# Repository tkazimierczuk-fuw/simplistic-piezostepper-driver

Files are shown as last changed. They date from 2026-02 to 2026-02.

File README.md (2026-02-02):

# A Simplistic Driver for Slip-Stick Piezo Positioners

This project presents a minimalistic, low-cost driver for slip-stick piezo positioners.

Conventional slip-stick piezo drivers typically rely on operational amplifiers to generate sawtooth waveforms. While this approach gives the most control over the stage, driving highly capacitive piezo loads with op-amps requires careful compensation and layout to avoid instability and self-oscillations.

In contrast, this driver avoids operational amplifiers altogether. Instead, the piezo load is driven directly using simple MOSFET stages. This significantly simplifies the circuit and improves robustness when dealing with capacitive loads, making the design well suited for ad-hoc, experimental, or budget-constrained setups.

The goal of this project is not ultimate performance, but practicality: providing a straightforward and reliable way to generate slip-stick drive signals with minimal component count and design overhead.

## Usage

The driver is straightforward - just connect your slip-stick piezo stage and use 3-way lever-switch to jog the stage. The step amplitude is fixed at 28 V and the step frequency is fixed (in the firmware) at 300 Hz. This values are suitable, e.g. for Attocube ANP series.

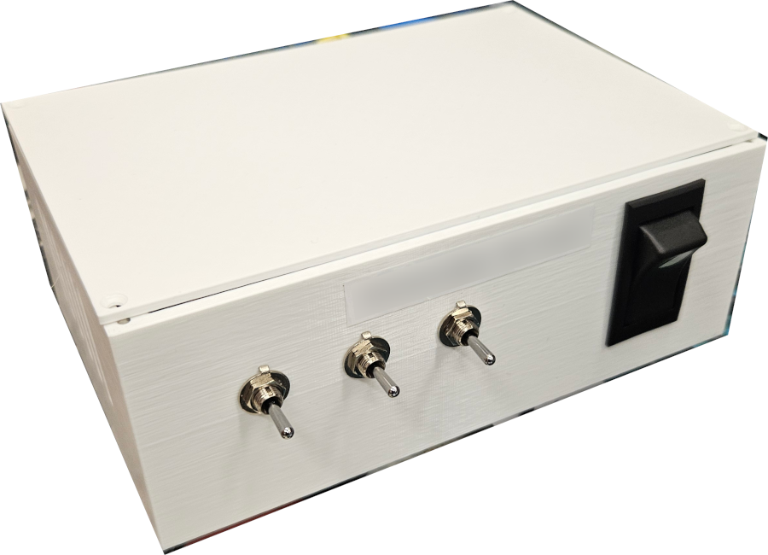
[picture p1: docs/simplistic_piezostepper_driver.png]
The driver enclosed in a 3D case


The circuit contains a PPTC resettable fuse which trips when we try to drive the short-circuit. It automatically resets upon switching the device off. 

## How it works

The driver generates the characteristic slip-stick waveform by charging and discharging the piezo capacitance directly through MOSFET switches, rather than through linear amplifiers. One stage provides a relatively slow voltage ramp (stick phase), while the other rapidly discharges the piezo (slip phase). Rapid charge/discharge is realized by linking the piezo to VCC/GND directly by a MOSFET. Slow ramp is realized by introducing an extra resistor R in series with the MOSFET. The time-constant of the slope is governed by a product of resistance R and the capacitance of the piezo stage.

Each of 3 modules has the same design:

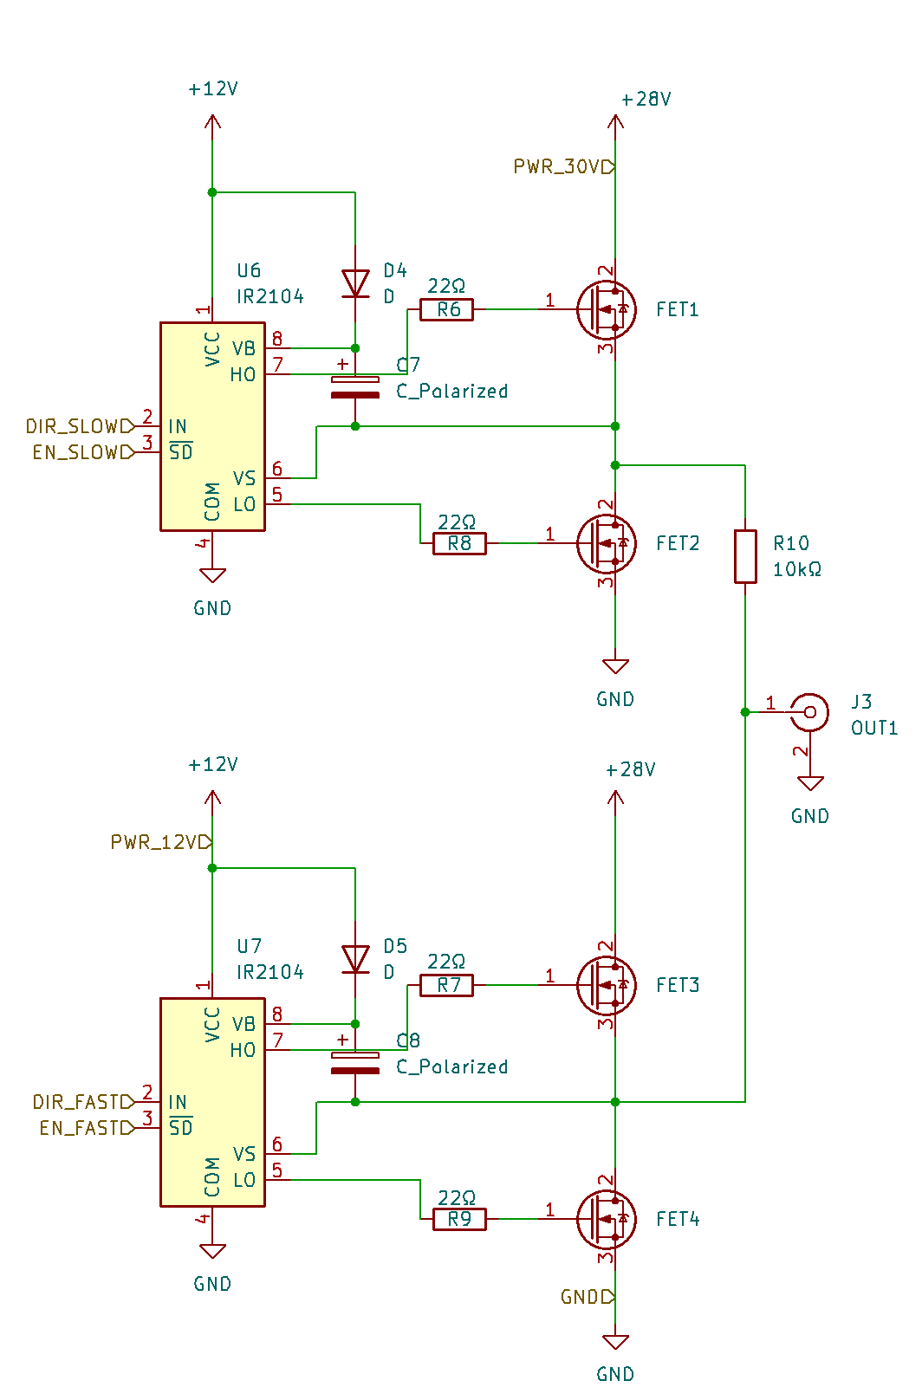
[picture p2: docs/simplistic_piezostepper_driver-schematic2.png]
Simplistic piezo stepper driver schematic


## What to buy (typical components)

Exact values and footprints are given in the schematics/PCB files, but the design generally requires only common parts:

- 12x N-channel MOSFETs, e.g. STP55NF06L
- 6x half-bridge driver, e.g. IR2104STRPBF
- 3x BNC connector, e.g. R-128
- 3x lever switch, e.g. 1-1825139-8
- 1x power switch, e.g. R13-220BA-01-BBG (oversized)
- Raspberry Pico
- SMD 1206 elements: 7x diode, resistors: 1x 1MΩ, 6x 100kΩ, 12x 22Ω, 3x 10kΩ
- THT capacitors
- a polymer fuse, e.g. 0ZCJ0020FF2E
- DC supply socket, e.g. PJ-063AH
- step-up converter, e.g. MT3608 

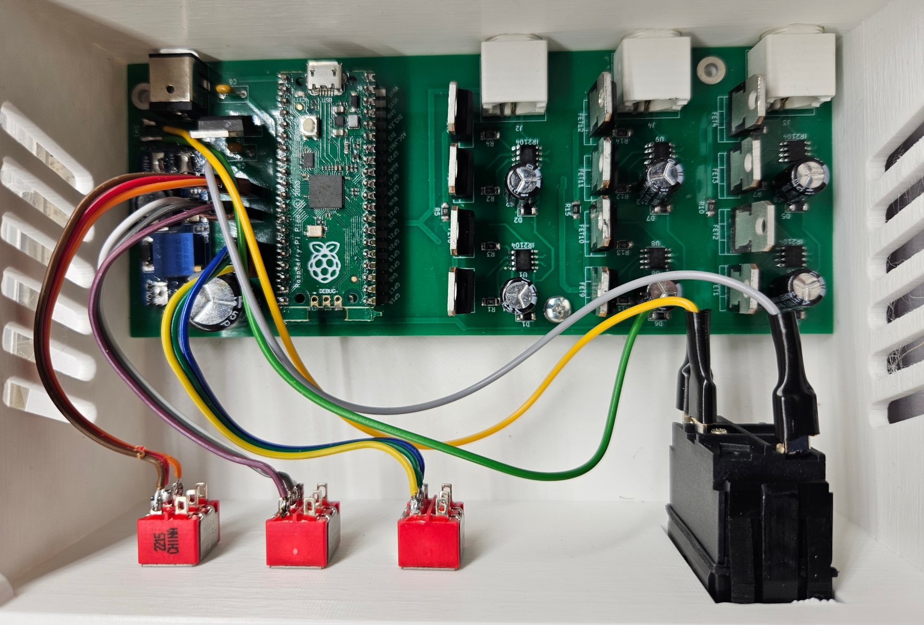
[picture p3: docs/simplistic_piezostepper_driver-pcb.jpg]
Fully populated PCB


## License & Disclaimer

This project is released under the MIT License. You are free to use, modify, and distribute it according to the terms of that license.

The design is provided as-is, without any warranties or guarantees of performance, safety, or suitability for any particular purpose. This is a research/DIY project; use it at your own risk.

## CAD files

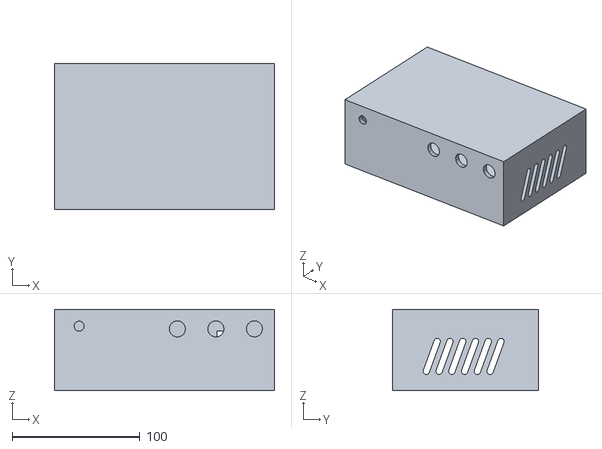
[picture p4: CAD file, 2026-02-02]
case/case_for_3dprint.stl
172.4 x 114.4 x 63.5

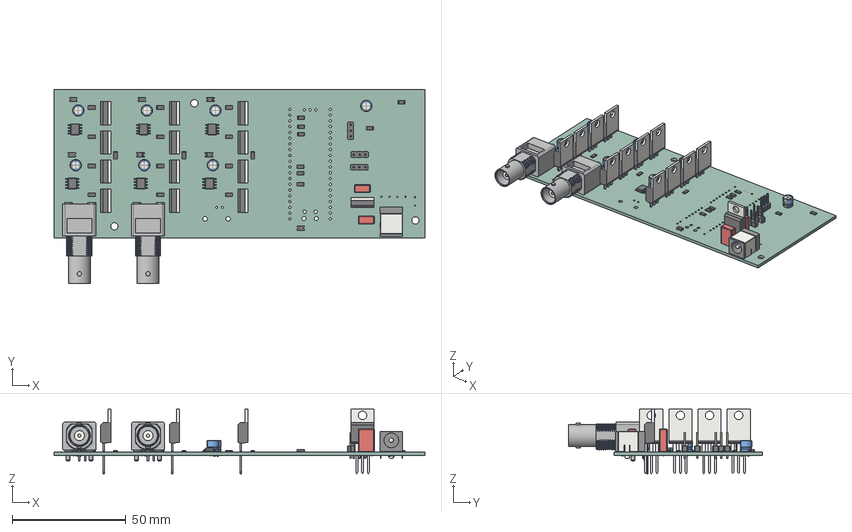
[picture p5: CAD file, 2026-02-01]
pcb/simplistic-piezostepper-driver.step
163.4 x 85.3 x 28.5 mm
C_Rect_L7.0mm_W3.5mm_P5.00mm x 2
D_1206_3216Metric x 7
SOIC-8_3.9x4.9mm_P1.27mm x 6
R_1206_3216Metric x 23
TO-220-3_Vertical x 13
BarrelJack_CUI_PJ-063AH_Horizontal
CP_Radial_D5.0mm_P2.00mm x 7
BNC_Amphenol_B6252HB-NPP3G-50_Horizontal x 2
Pico
PinHeader_1x03_P2.54mm_Vertical x 3
homemade_attocube_PCB

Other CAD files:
case/case_for_3dprint.ipt

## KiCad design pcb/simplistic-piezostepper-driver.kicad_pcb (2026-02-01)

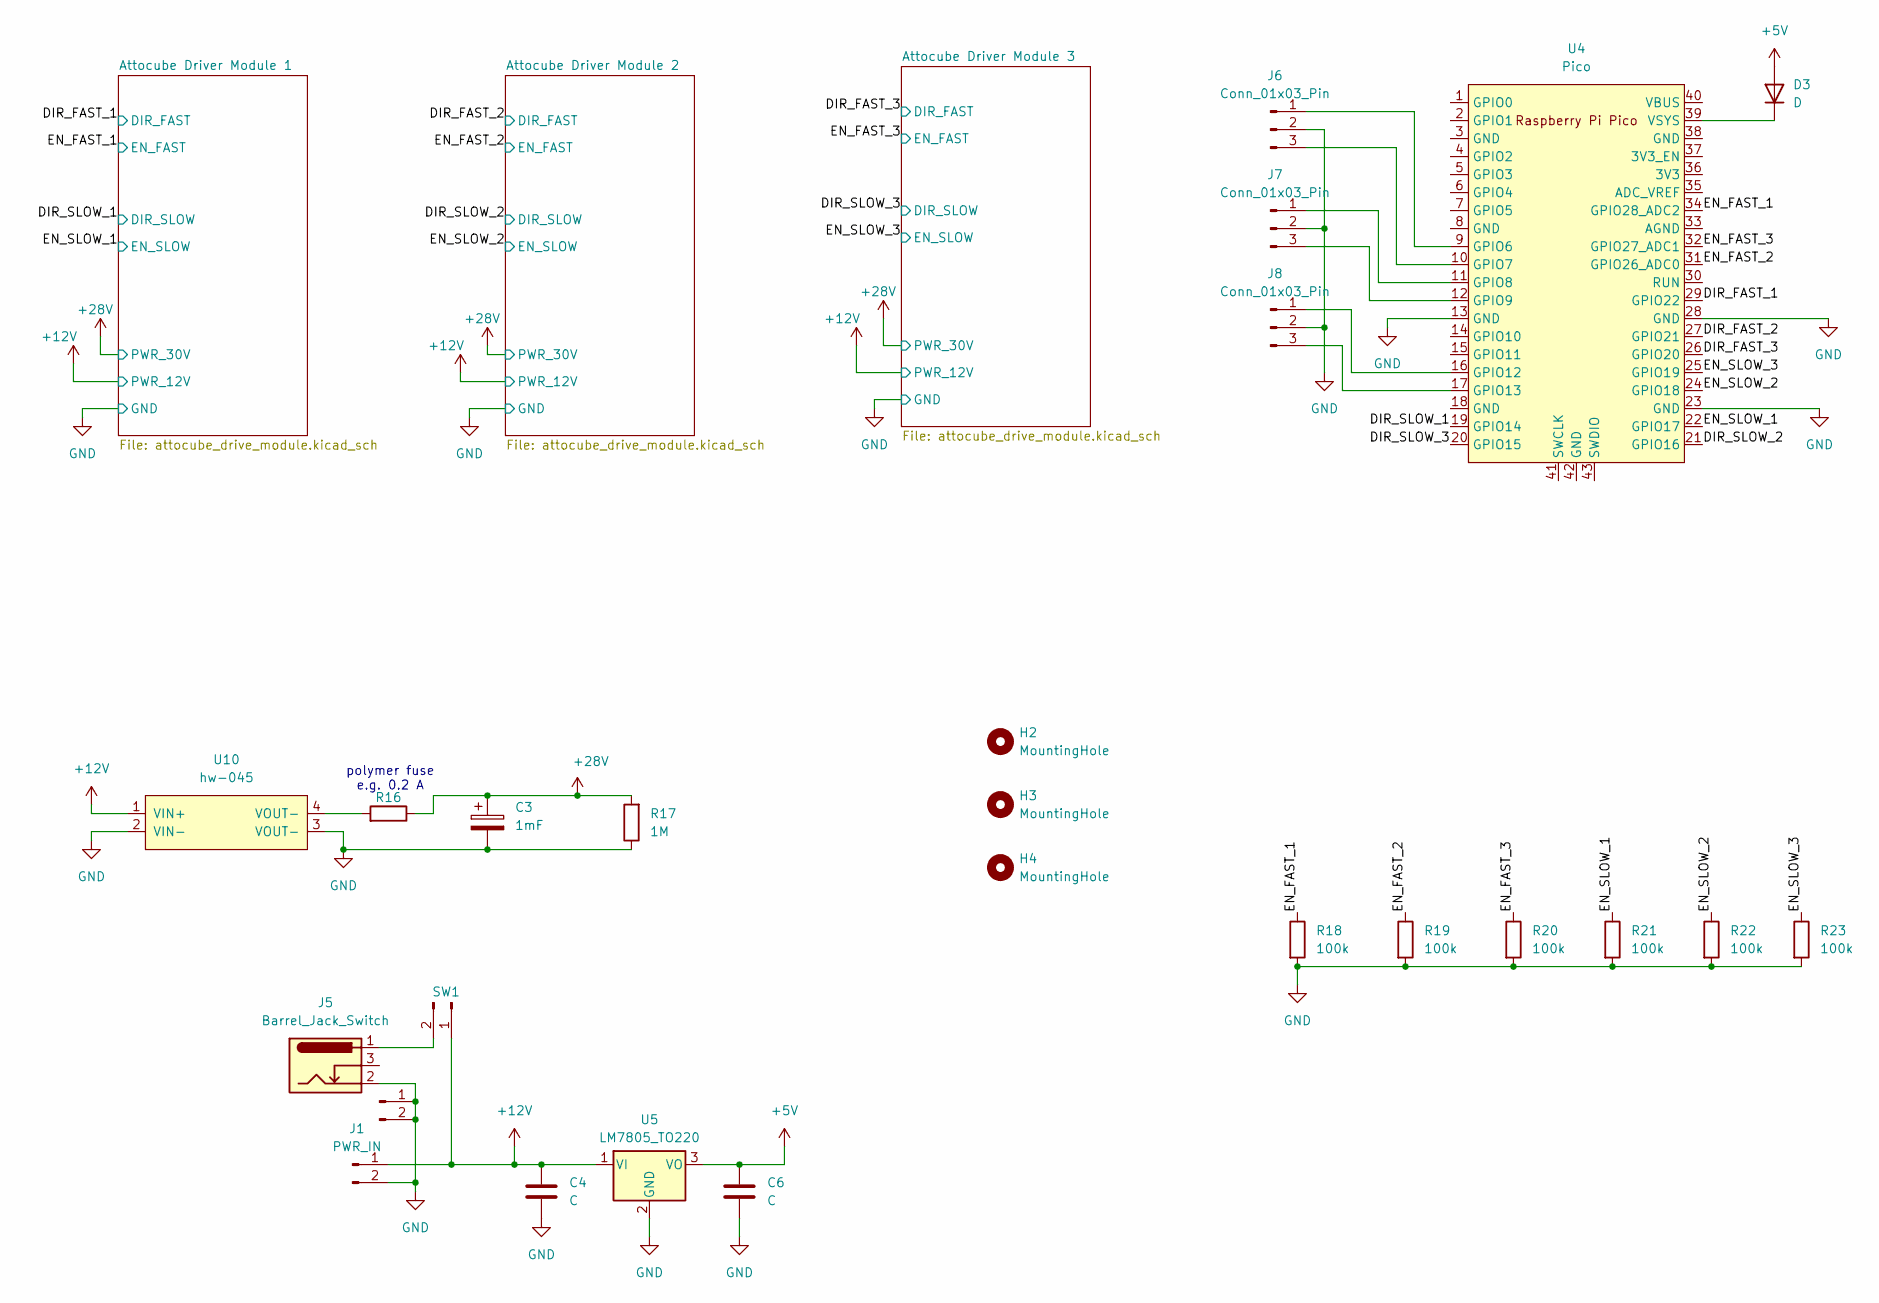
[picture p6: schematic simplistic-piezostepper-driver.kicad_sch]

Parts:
C3: 1mF; CP_Radial_D5.0mm_P2.00mm
C4, C6: C; C_Rect_L7.0mm_W3.5mm_P5.00mm
D3: D; D_1206_3216Metric_Pad1.42x1.75mm_HandSolder
H2, H3, H4: MountingHole; MountingHole_3.2mm_M3_Pad
J1: PWR_IN; SolderWire-0.1sqmm_1x02_P3.6mm_D0.4mm_OD1mm
J5: Barrel_Jack_Switch; BarrelJack_CUI_PJ-063AH_Horizontal
J6, J7, J8: Conn_01x03_Pin; PinHeader_1x03_P2.54mm_Vertical
J10: Conn_01x02_Pin; SolderWire-0.1sqmm_1x02_P3.6mm_D0.4mm_OD1mm
R16: 10?; R_1206_3216Metric_Pad1.30x1.75mm_HandSolder
R17: 1M; R_1206_3216Metric_Pad1.30x1.75mm_HandSolder
R18, R19, R20, R21, R22, R23: 100k; R_1206_3216Metric_Pad1.30x1.75mm_HandSolder
SW1: Conn_01x02_Pin; SolderWire-0.1sqmm_1x02_P3.6mm_D0.4mm_OD1mm
U4: Pico; RPi_Pico_SMD_TH
U5: LM7805_TO220; TO-220-3_Vertical
U10: hw-045

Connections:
+5V: C6.1, D3.2 (A), U5.3 (VO)
+12V: C4.1, J1.1, SW1.1, U5.1 (VI), U10.1 (VIN+); also elsewhere on the board
+28V: C3.1, R16.1, R17.2; also elsewhere on the board
/DIR_FAST_1: U4.29 (GPIO22); also elsewhere on the board
/DIR_FAST_2: U4.27 (GPIO21); also elsewhere on the board
/DIR_FAST_3: U4.26 (GPIO20); also elsewhere on the board
/DIR_SLOW_1: U4.19 (GPIO14); also elsewhere on the board
/DIR_SLOW_2: U4.21 (GPIO16); also elsewhere on the board
/DIR_SLOW_3: U4.20 (GPIO15); also elsewhere on the board
/EN_FAST_1: R18.1, U4.34 (GPIO28_ADC2); also elsewhere on the board
/EN_FAST_2: R19.1, U4.31 (GPIO26_ADC0); also elsewhere on the board
/EN_FAST_3: R20.1, U4.32 (GPIO27_ADC1); also elsewhere on the board
/EN_SLOW_1: R21.1, U4.22 (GPIO17); also elsewhere on the board
/EN_SLOW_2: R22.1, U4.24 (GPIO18); also elsewhere on the board
/EN_SLOW_3: R23.1, U4.25 (GPIO19); also elsewhere on the board
GND: C3.2, C4.2, C6.2, J1.2, J5.2, J6.2, J7.2, J8.2, J10.1, J10.2, R17.1, R18.2, R19.2, R20.2, R21.2, R22.2, R23.2, U4.13 (GND), U4.23 (GND), U4.28 (GND), U5.2 (GND), U10.2 (VIN-), U10.3 (VOUT-); also elsewhere on the board
unnamed: D3.1 (K), U4.39 (VSYS)
unnamed: J6.1, U4.9 (GPIO6)
unnamed: J6.3, U4.10 (GPIO7)
unnamed: J7.1, U4.11 (GPIO8)
unnamed: J7.3, U4.12 (GPIO9)
unnamed: J8.1, U4.16 (GPIO12)
unnamed: J8.3, U4.17 (GPIO13)
unnamed: R16.2, U10.4 (VOUT-)
unnamed: J5.1, SW1.2

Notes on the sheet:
polymer fuse e.g. 0.2 A

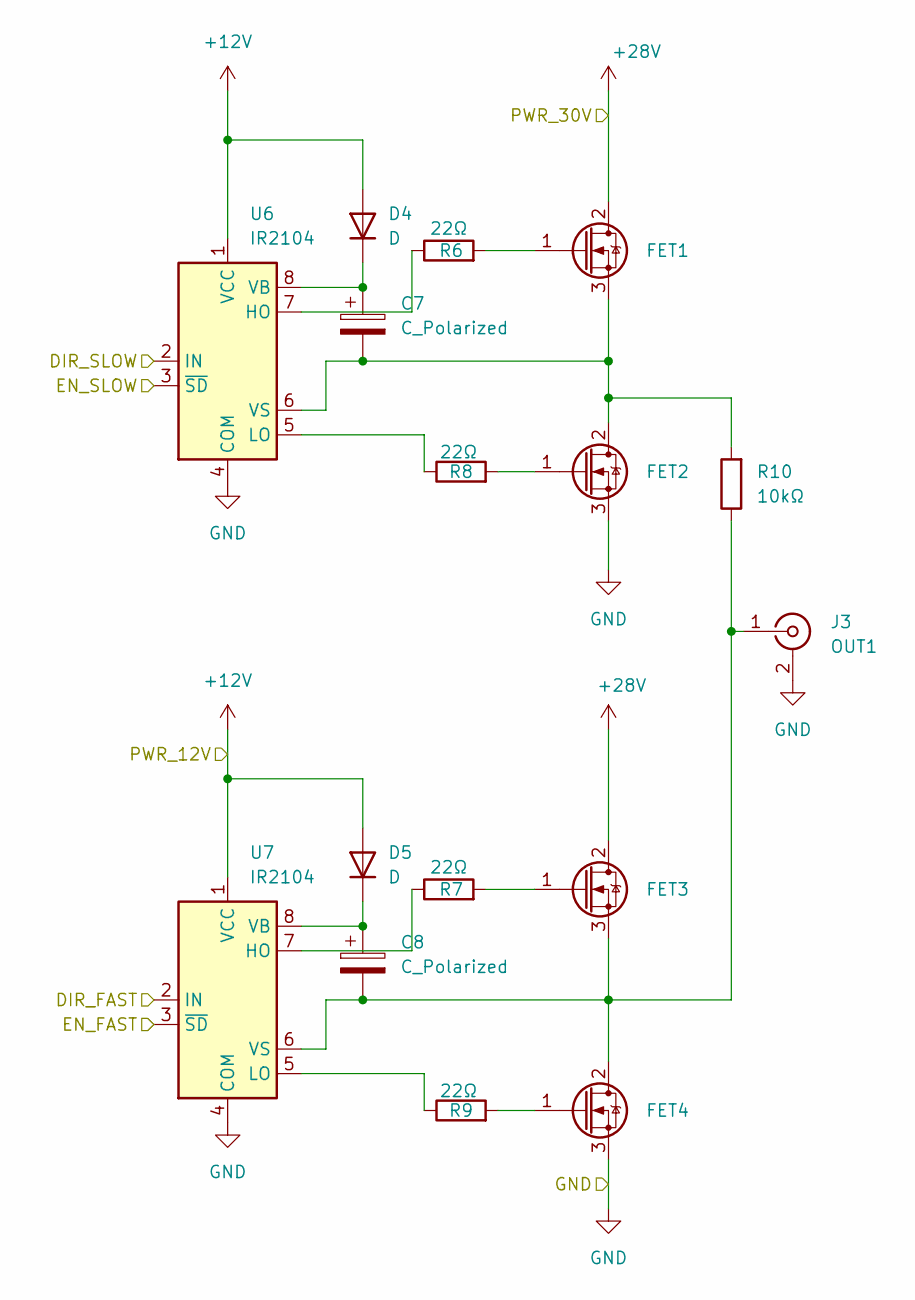
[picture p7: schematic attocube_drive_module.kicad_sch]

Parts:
C7, C8: C_Polarized; CP_Radial_D5.0mm_P2.00mm
D4, D5: D; D_1206_3216Metric_Pad1.42x1.75mm_HandSolder
FET1, FET2, FET3, FET4: Q_NMOS_Depletion_GDS; TO-220-3_Vertical
J3: OUT1; BNC_Amphenol_B6252HB-NPP3G-50_Horizontal
R6, R7, R8, R9: 22Ω; R_1206_3216Metric_Pad1.30x1.75mm_HandSolder
R10: 10kΩ; R_1206_3216Metric_Pad1.30x1.75mm_HandSolder
U6, U7: IR2104; SOIC-8_3.9x4.9mm_P1.27mm

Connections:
+12V: D4.2 (A), D5.2 (A), U6.1 (VCC), U7.1 (VCC); also elsewhere on the board
+28V: FET1.2 (D), FET3.2 (D); also elsewhere on the board
/DIR_FAST_1: U7.2 (IN); also elsewhere on the board
/DIR_SLOW_1: U6.2 (IN); also elsewhere on the board
/EN_FAST_1: U7.3 (~SD); also elsewhere on the board
/EN_SLOW_1: U6.3 (~SD); also elsewhere on the board
GND: FET2.3 (S), FET4.3 (S), J3.2 (Ext), U6.4 (COM), U7.4 (COM); also elsewhere on the board
unnamed: C7.1, D4.1 (K), U6.8 (VB)
unnamed: C8.1, D5.1 (K), U7.8 (VB)
unnamed: FET1.1 (G), R6.2
unnamed: C7.2, FET1.3 (S), FET2.2 (D), R10.2, U6.6 (VS)
unnamed: FET2.1 (G), R8.2
unnamed: FET3.1 (G), R7.2
unnamed: C8.2, FET3.3 (S), FET4.2 (D), J3.1 (In), R10.1, U7.6 (VS)
unnamed: FET4.1 (G), R9.2
unnamed: R6.1, U6.7 (HO)
unnamed: R8.1, U6.5 (LO)
unnamed: R7.1, U7.7 (HO)
unnamed: R9.1, U7.5 (LO)

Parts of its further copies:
C1, C2, C11, C12: C_Polarized; CP_Radial_D5.0mm_P2.00mm
D1, D2, D6, D7: D; D_1206_3216Metric_Pad1.42x1.75mm_HandSolder
FET5, FET6, FET7, FET8, FET9, FET10, FET11, FET12: Q_NMOS_Depletion_GDS; TO-220-3_Vertical
J2, J4: OUT1; BNC_Amphenol_B6252HB-NPP3G-50_Horizontal
R1, R2, R3, R4, R11, R12, R13, R14: 22Ω; R_1206_3216Metric_Pad1.30x1.75mm_HandSolder
R5, R15: 10kΩ; R_1206_3216Metric_Pad1.30x1.75mm_HandSolder
U1, U2, U8, U9: IR2104; SOIC-8_3.9x4.9mm_P1.27mm

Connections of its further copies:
+12V: D1.2 (A), D2.2 (A), D6.2 (A), D7.2 (A), U1.1 (VCC), U2.1 (VCC), U8.1 (VCC), U9.1 (VCC); also elsewhere on the board
+28V: FET5.2 (D), FET7.2 (D), FET9.2 (D), FET11.2 (D); also elsewhere on the board
/DIR_FAST_2: U2.2 (IN); also elsewhere on the board
/DIR_FAST_3: U9.2 (IN); also elsewhere on the board
/DIR_SLOW_2: U1.2 (IN); also elsewhere on the board
/DIR_SLOW_3: U8.2 (IN); also elsewhere on the board
/EN_FAST_2: U2.3 (~SD); also elsewhere on the board
/EN_FAST_3: U9.3 (~SD); also elsewhere on the board
/EN_SLOW_2: U1.3 (~SD); also elsewhere on the board
/EN_SLOW_3: U8.3 (~SD); also elsewhere on the board
GND: FET6.3 (S), FET8.3 (S), FET10.3 (S), FET12.3 (S), J2.2 (Ext), J4.2 (Ext), U1.4 (COM), U2.4 (COM), U8.4 (COM), U9.4 (COM); also elsewhere on the board
unnamed: C1.1, D1.1 (K), U1.8 (VB)
unnamed: C2.1, D2.1 (K), U2.8 (VB)
unnamed: C11.1, D6.1 (K), U8.8 (VB)
unnamed: C12.1, D7.1 (K), U9.8 (VB)
unnamed: FET5.1 (G), R1.2
unnamed: C1.2, FET5.3 (S), FET6.2 (D), R5.2, U1.6 (VS)
unnamed: FET6.1 (G), R3.2
unnamed: FET7.1 (G), R2.2
unnamed: C2.2, FET7.3 (S), FET8.2 (D), J2.1 (In), R5.1, U2.6 (VS)
unnamed: FET8.1 (G), R4.2
unnamed: FET9.1 (G), R11.2
unnamed: C11.2, FET9.3 (S), FET10.2 (D), R15.2, U8.6 (VS)
unnamed: FET10.1 (G), R13.2
unnamed: FET11.1 (G), R12.2
unnamed: C12.2, FET11.3 (S), FET12.2 (D), J4.1 (In), R15.1, U9.6 (VS)
unnamed: FET12.1 (G), R14.2
unnamed: R1.1, U1.7 (HO)
unnamed: R3.1, U1.5 (LO)
unnamed: R2.1, U2.7 (HO)
unnamed: R4.1, U2.5 (LO)
unnamed: R11.1, U8.7 (HO)
unnamed: R13.1, U8.5 (LO)
unnamed: R12.1, U9.7 (HO)
unnamed: R14.1, U9.5 (LO)

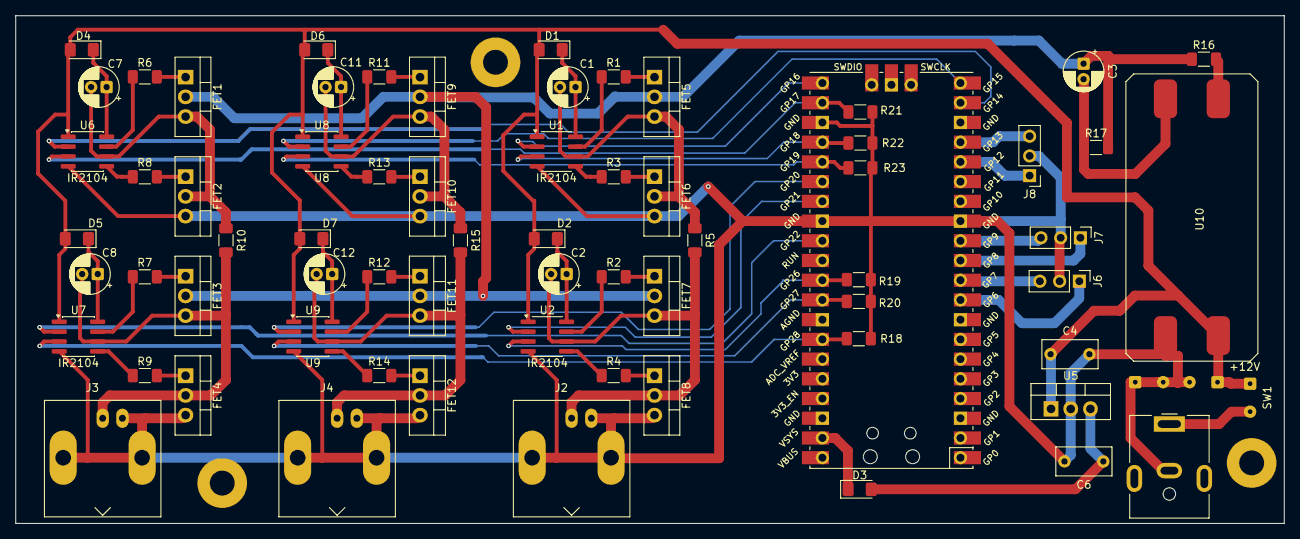
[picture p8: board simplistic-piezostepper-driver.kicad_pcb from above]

Board: 2 copper layers, 163.4 x 65.4 mm, 73 parts (0 on the bottom side), 61 nets.

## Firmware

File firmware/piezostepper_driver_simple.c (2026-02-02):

#include <stdio.h>
#include "pico/stdlib.h"

const int STEP_FREQ = 500;

// Channel pin definitions
typedef struct {
    int up_control_pin;
    int down_control_pin;
    int dir_fast_pin;
    int dir_slow_pin;
    int en_fast_pin;
    int en_slow_pin;
} ChannelPins;

// Channel 1 pins
const ChannelPins channel1_pins = {
    .up_control_pin = 6,
    .down_control_pin = 7,
    .dir_fast_pin = 22,
    .dir_slow_pin = 14,
    .en_fast_pin = 28,
    .en_slow_pin = 17
};

// Channel 2 pins
const ChannelPins channel2_pins = {
    .up_control_pin = 8,
    .down_control_pin = 9,
    .dir_fast_pin = 21,
    .dir_slow_pin = 16,
    .en_fast_pin = 26,
    .en_slow_pin = 18
};

// Channel 3 pins
const ChannelPins channel3_pins = {
    .up_control_pin = 12,
    .down_control_pin = 13,
    .dir_fast_pin = 20,
    .dir_slow_pin = 15,
    .en_fast_pin = 27,
    .en_slow_pin = 19
};

const ChannelPins* all_channels[] = {&channel1_pins, &channel2_pins, &channel3_pins};
const int num_channels = sizeof(all_channels) / sizeof(all_channels[0]);


typedef enum {
    IDLE,
    SLOW_UP,
    SLOW_DOWN,
    FAST_UP,
    FAST_DOWN
} ChannelState;

ChannelState state[] = {IDLE, IDLE, IDLE};



void initialize_gpio() {
    for (int i = 0; i < num_channels; i++) {
        const ChannelPins* channel = all_channels[i];

        // Configure control pins as inputs with pull-ups
        gpio_init(channel->up_control_pin);
        gpio_set_dir(channel->up_control_pin, GPIO_IN);
        gpio_pull_up(channel->up_control_pin);

        gpio_init(channel->down_control_pin);
        gpio_set_dir(channel->down_control_pin, GPIO_IN);
        gpio_pull_up(channel->down_control_pin);

        // Configure dir and en pins as outputs, initially low
        const int output_pins[] = {
            channel->dir_fast_pin, channel->dir_slow_pin,
            channel->en_fast_pin, channel->en_slow_pin
        };
        for (int j = 0; j < sizeof(output_pins) / sizeof(output_pins[0]); j++) {
            uint pin = output_pins[j];
            gpio_set_dir(pin, GPIO_OUT);
            gpio_init(pin);
            gpio_set_dir(pin, GPIO_OUT);
            gpio_put(pin, 0);
            state[i] = IDLE;
        }
    }
}

const int SLOW_STATE_RATIO = 4 ; // relative duration of the slow rise/fall phase
const int DELAY_US = 1000000L / (STEP_FREQ * num_channels * (4+SLOW_STATE_RATIO) );


int main()
{
    stdio_init_all();

    initialize_gpio();

    int cycles_in_slow_state = 0; 

    while (true) {
        for(int ch = 0; ch < num_channels; ch++) {

            bool going_up = (gpio_get(all_channels[ch]->up_control_pin) == 0);
            bool going_down = !going_up && (gpio_get(all_channels[ch]->down_control_pin) == 0);
            if(going_up) {
                switch(state[ch]) {
                    case IDLE:
                        gpio_put(all_channels[ch]->en_slow_pin, false);
                        state[ch] = FAST_UP;
                        gpio_put(all_channels[ch]->dir_fast_pin, true);
                        gpio_put(all_channels[ch]->en_fast_pin, true);
                        break;
                    case FAST_UP:
                    case SLOW_UP: // this case is not part of the standard scenario, but might happen upon quick reversal
                        gpio_put(all_channels[ch]->en_fast_pin, false);
                        gpio_put(all_channels[ch]->dir_fast_pin, false);
                        state[ch] = SLOW_DOWN;
                        cycles_in_slow_state = 0;
                        gpio_put(all_channels[ch]->dir_slow_pin, false);
                        gpio_put(all_channels[ch]->en_slow_pin, true);
                        break;
                    case SLOW_DOWN:
                        cycles_in_slow_state++;
                        if(cycles_in_slow_state >= SLOW_STATE_RATIO)
                        {
                            gpio_put(all_channels[ch]->en_slow_pin, false);
                            state[ch] = FAST_DOWN;
                            gpio_put(all_channels[ch]->dir_fast_pin, false);
                            gpio_put(all_channels[ch]->en_fast_pin, true);
                        }
                        break;
                    case FAST_DOWN:
                        gpio_put(all_channels[ch]->en_fast_pin, false);
                        state[ch] = IDLE;
                        gpio_put(all_channels[ch]->dir_slow_pin, false);
                        gpio_put(all_channels[ch]->en_slow_pin, true);
                        break;                    
                }
            }

            //-------
            if(going_down) {
                switch(state[ch]) {
                    case IDLE:
                    case SLOW_DOWN: // this case is not expected in typical scenario, but might occur upon quick direction reversal
                        state[ch] = SLOW_UP;
                        cycles_in_slow_state = 0;
                        gpio_put(all_channels[ch]->dir_slow_pin, true);
                        gpio_put(all_channels[ch]->en_slow_pin, true);
                        break;
                    case SLOW_UP:
                        cycles_in_slow_state++;
                        if(cycles_in_slow_state >= SLOW_STATE_RATIO) {
                            gpio_put(all_channels[ch]->en_slow_pin, false);
                            state[ch] = FAST_UP;
                            gpio_put(all_channels[ch]->dir_fast_pin, true);
                            gpio_put(all_channels[ch]->en_fast_pin, true);
                        }
                        break;
                    case FAST_UP:
                        state[ch] = FAST_DOWN;
                        gpio_put(all_channels[ch]->dir_fast_pin, false);
                        gpio_put(all_channels[ch]->en_fast_pin, true);
                        break;
                    case FAST_DOWN:
                        gpio_put(all_channels[ch]->en_fast_pin, false);
                        state[ch] = IDLE;
                        gpio_put(all_channels[ch]->dir_slow_pin, false);
                        gpio_put(all_channels[ch]->en_slow_pin, true);
                        break;    
                }
            }

            sleep_us(DELAY_US);
        }
    }
}

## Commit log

2026-02-01 Added a KiCAD schematic
    [attocube_drive_module.kicad_sch, simplistic-piezostepper-driver.kicad_pcb, simplistic-piezostepper-driver.kicad_sch, simplistic-piezostepper-driver.step]
2026-02-02 Uploaded: firmware and case 3D model
    [case_for_3dprint.ipt, case_for_3dprint.stl]
